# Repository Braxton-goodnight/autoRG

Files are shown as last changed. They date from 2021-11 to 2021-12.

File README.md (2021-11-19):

# autoRG
# Initial Developers: Braxton Goodnight, Rameen Forghani, Charles Latchoumane, Lohitash Karumbaiah
Includes all software code (GUI1 and GUI_scale_calibration), firmware (Arduino IDE), STL files for 3D printing, bill of commercial materials, and SOPs for the assembly of the autoRG system, downloading and initializing software, calibrating the system, and executing the assay.

# Requirements
* Matlab 2020a or newer (Earlier versions may be able to run system, but is not guaranteed)
* Windows 10 Computer
* Circuit Playground Express (CPX) (Adafruit Industries) and all other commercial electronics (see AutoRG_Assembly_SOP and Electronics_Bill_of_Materials) for CPX bootloading and assay execution

# Purpose
The autoRG system was developed to assist researchers in neurological studies of rat motor behavior. The system's hardware, software, and firmware was developed to be user-friendly, modular, reproducible, and low-cost to maximize objectivity and access to in vivo functional assessments. 

# Version 1
autoRG v1 utilizes a discrete, 7-stage training system that requires the user to manually determine when the rat has passed the criteria for that stage and select the correct stage for each rat in the menu options prior to each session. Modulation of the handle location, trigger threshold, and pellet dispenses is controlled by the update_param function. Current criterion for stage advancement using default training protocol: 
* Stage 1 - 60 successes each in two consecutive sessions
* Stage 2 - 45 successes in single session
* Stage 3 - 30 successes in single session
* Stage 4 - 30 successes in single session
* Stage 5 - 30 successes in single session
* Stage 6 - 30 successes in single session
* Stage 7 - 30 successes in single session, or until desired efficiency (# of successes / total # of reaches) is reached

# Contributions
Users can contribute to this repository by customizing the update_param function to introduce their own training schemes that train the rats more rapidly or reinforce a slightly different behavior. Further, fixes to any bugs that may arise across operating systems are encouraged. Potential training schemes to implement: 
* Continuous stage advancement - System advances rat to next stage automatically by automated measurement of some metric(s)
* Adaptive Training - System automatically progresses or modulates the trigger threshold (e.g., median of prior 10 reaches) and handle location with upper and lower boundaries
* Machine Learning - System learns which metrics are predictive of future successes or future failures and uses this information to modulate the assay parameters (handle location, trigger threshold, pellet dispenses)

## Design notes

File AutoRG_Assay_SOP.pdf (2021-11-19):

Standard Operating Procedure: Automated Reach-to-Grasp Task (AutoRG)

### 1. Purpose

1.1. This SOP describes the procedures necessary to properly utilize the hardware and software of the AutoRG system to assess forelimb motor function in rats.
1.2. This SOP utilizes the default, 7-stage training scheme provided in the standard code
1.3. This SOP assumes that the following processes are already completed:
1.3.1. The apparatus is completely assembled and primed (see: AutoRG_Assembly_SOP)
1.3.2. The software has been downloaded/integrated with a Windows computer (see: AutoRG_SoftwareInitialization_SOP)
1.3.3. The system has been calibrated and the calibration file is accessible (see: AutoRG_Calibration_SOP)

### 2. Equipment and Terminology

2.1.Cage – Refers to acrylic cage in which the rat is placed for the duration of the session

2.2. Stage – Refers collectively to the 4 stage blocks that are pre-assembled into one single stage, of which the cage is placed on top.
2.3. Handle Base – Refers to the base to which the linear motion rail is affixed
2.4. CPX – Refers to the Circuit Playground Express
2.5. CRICKIT – Refers to CRICKIT board that is attached to the CPX
2.6. Pellet Dispenser – Refers collectively to the Pellet Dispense Base and Food Silo that compose the pellet dispense apparatus
2.7. Pellet Dispense Base – Refers to base of Pellet Dispenser that has the 4 legs and includes an insertion point for the Pellet Servo
2.8. Pellet Servo Actuator – Refers to circular piece of Pellet Dispenser that connects to Pellet Servo and rotates within the Pellet Dispenser to allow pellets to be delivered
2.9. Food Silo – Refers to top of Pellet Dispenser that holds the reservoir of pellets
2.10. Pellet Dispense Tower – Refers to the tower block on which the pellet dispenser sits

2.11. Pellet Receptacle – Refers to the receptacle that receives the pellet tubing from the pellet dispenser and re-directs the pellet into the slit of the cage
2.12. Pellet Tubing – Refers to the rubber tubing that connects the pellet dispenser to the pellet receptacle (Saint-Gobain Tygon S3 E-3603 Food Tubing)
2.13. Pellet Servo – Refers to the continuous servo that actuates the pellet dispenser
2.14. Calibration Knob – Refers to knob that is used to calibrate the continuous servo
2.15. Load Cell – Refers to mini load attached to handle
2.16. Load Cell Carriage – Refers to bottom half of load cell casing that connects load cell to linear motion rail
2.17. Load Cell Handle Adapter – Refers to top half of load cell casing that connects load cell to handle
2.18. Proximal Servo Arm Adapter – Refers to servo arm adapter that connects directly to positional servo arm
2.19. Distal Servo Arm Adapter – Refers to servo arm adapter that connects the proximal servo arm to the high cube intermediate joint
2.20. High Cube Intermediate Joint – Refers to joint connecting the distal servo arm adapter to the load cell rail adapter
2.21. Handle – Refers to 1.5mm AF hex key that is affixed to the load cell apparatus
2.22. Load Cell Apparatus – Refers to load cell, load cell casing components, and rail attachment component
2.23. Rail – Refers to the 100mm-long linear motion rail on which the load cell apparatus sits
2.24. Positional Servo – Refers to the positional servo that actuates the movement of the load cell apparatus to modulate the handle distance
2.25. Positional Servo Casing – Refers to SLA-printed casing that encloses the Positional Servo and sits at the back of the Handle Base
2.26. Qwiic Scale – Refers to red analog-to-digital converter that connects the load cell to the Qwiic Adapter.

2.27. Qwiic Adapter – Refers to the component that receives a plug from the Qwiic Scale and projects wires to the CRICKIT and CPX boards.
2.28. CPX Holder – Refers to component where CPX rests; snaps into back of Pellet Dispense Tower.
2.29. Power Cord – Refers to the cord connecting the CRICKIT board to power
2.30. USB Cord – Refers to the cord connecting the CPX (micro-USB) to the computer (USB)
2.31. GUI1 – Refers to the primary MatLab graphic user interface through which the AutoRG assay is run
2.32. GUI1 Code – Refers to the code underlying GUI1
2.33. Calibration GUI – Refers to the MatLab graphic user interface that creates the calibration file
2.34. Calibration GUI Code – Refers to the code underlying the calibration GUI
2.35. Trigger Threshold: Minimum force required to trigger a successful trial and a pellet dispense

### 3. Assay Procedure

3.1. Plug in USB from CPX into the computer, ensure power cord is plugged into outlet and CRICKIT
3.2. Switch CPX on. Click reset button in center of CPX.

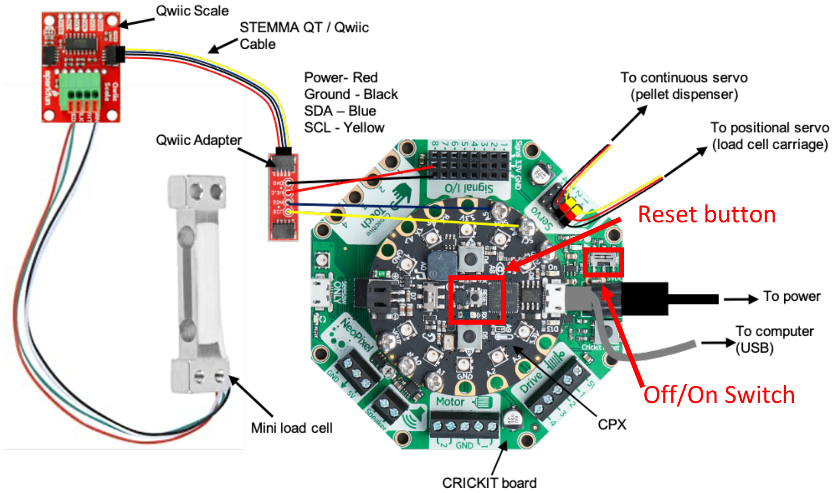
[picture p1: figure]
Reset button; Off/On Switch

3.3.Open GUI1.m on MatLab

3.4. Click “Run” to open GUI1

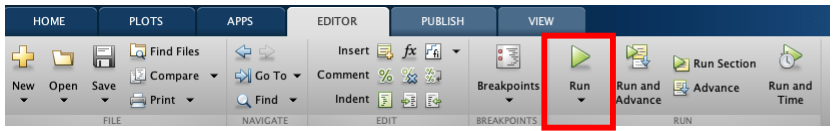
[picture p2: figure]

3.5. In the textbox beside “Port”, enter the port designation for your USB serial connection (CPX) (e.g. COM5). Click the yellow “CPX Connect” button below.
3.5.1. To check the port designation for your CPX, go to Device Manager > Click on “Ports” > See port designation for “USB Serial Connection”
3.5.2. Entering the COM designation directly in the GUI1 code saves a default COM designation so that you do not have to type in the designation each time (see: AutoRG_SoftwareInitialization_SOP). Note that the COM designation will change if a different CPX is used.
3.5.3. Check that a green “COM[] CONNECTED” box appears (where [] is the number of your COM designation)

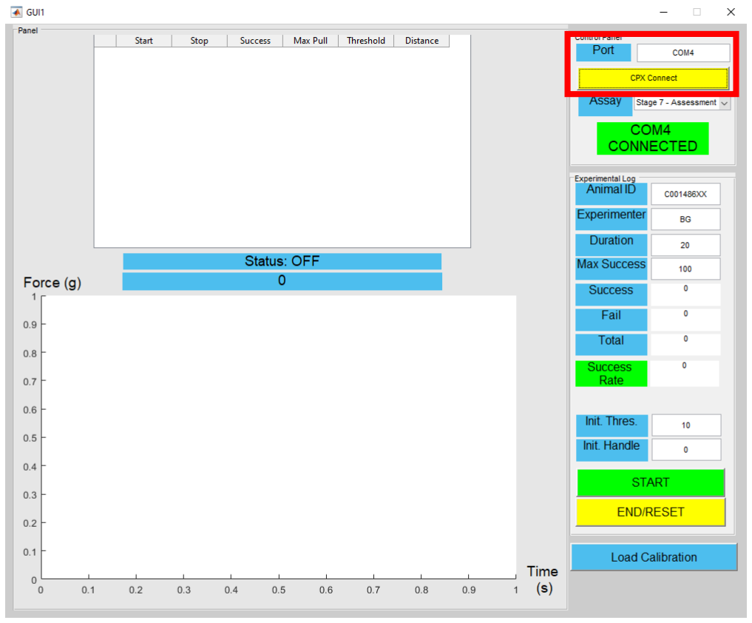
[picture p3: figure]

3.6. Select the Appropriate stage for the current rat in the dropdown box beside “Assay”

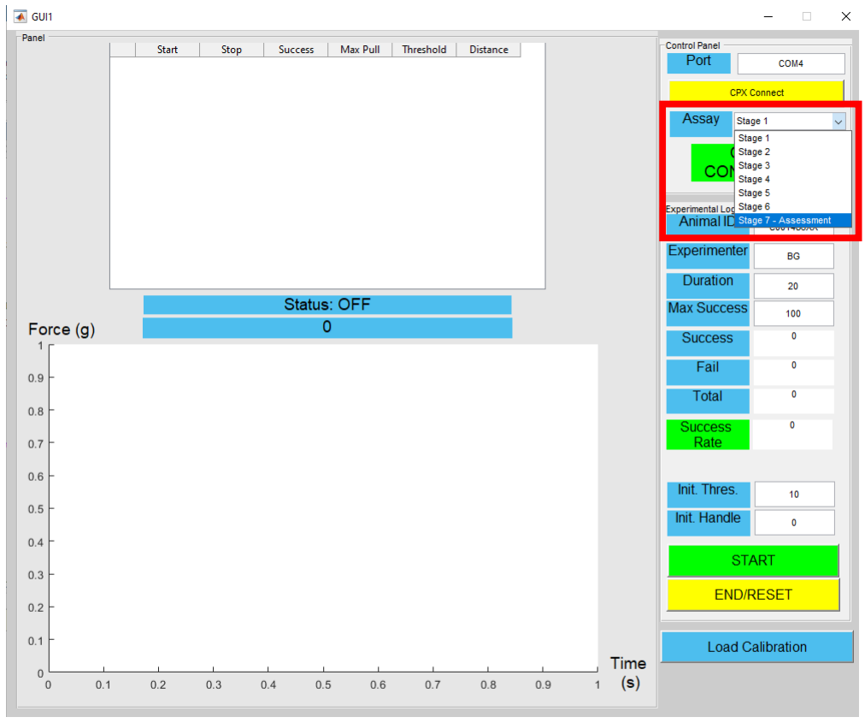
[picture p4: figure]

3.7. Enter any identifying number/code for the current rat in the textbox beside “Animal ID”

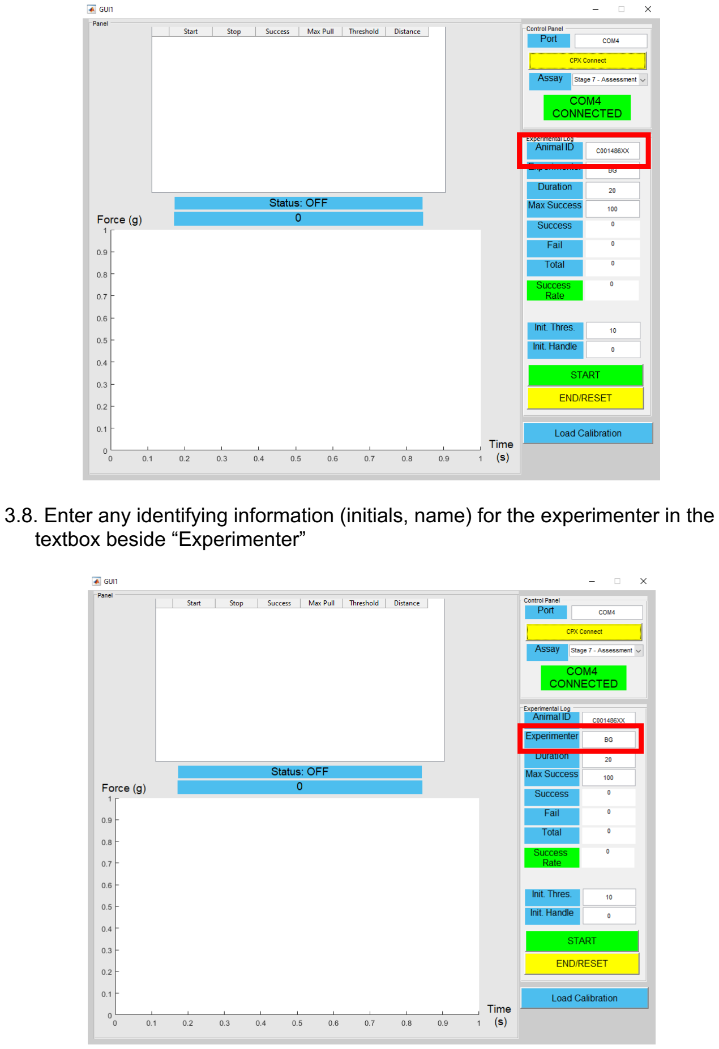
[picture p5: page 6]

3.8. Enter any identifying information (initials, name) for the experimenter in the textbox beside “Experimenter”

3.9. To change the default session duration: Enter desired session duration in minutes in the textbox beside “Duration”
3.9.1. Default: 20 minutes
3.9.2. If user desires to change session duration permanently, it is recommended to make this change directly in the GUI1 code. See AutoRG_SoftwareCustomization for more information

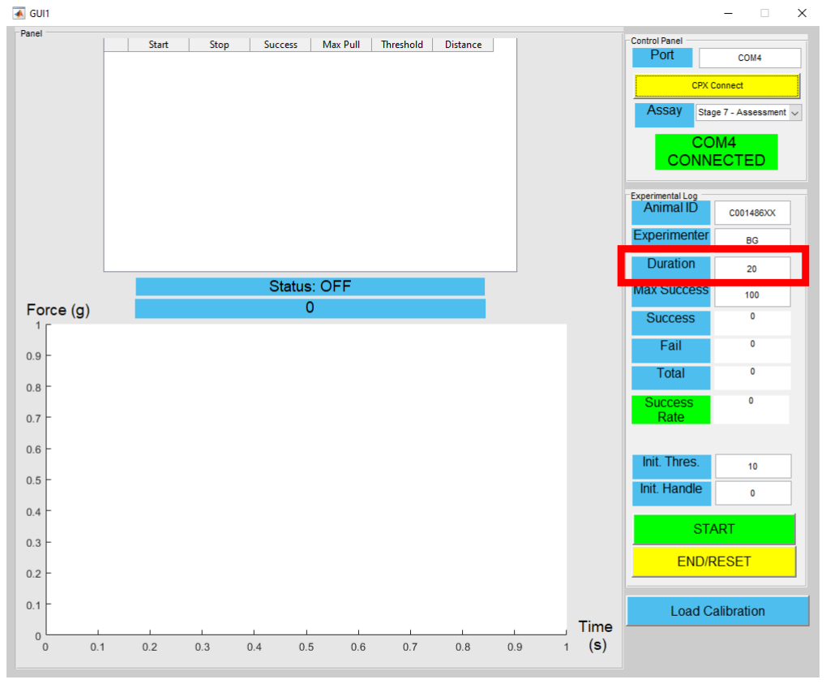
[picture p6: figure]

3.10. To change the default maximum number of successful trials for a given session: Enter desired maximum number of successful trials in the textbox beside “Max Success”
3.10.1. Default: 100 successes
3.10.2. If user desires to change maximum successes permanently, it is recommended to make this change directly in the GUI1 code. See AutoRG_SoftwareCustomization for more information

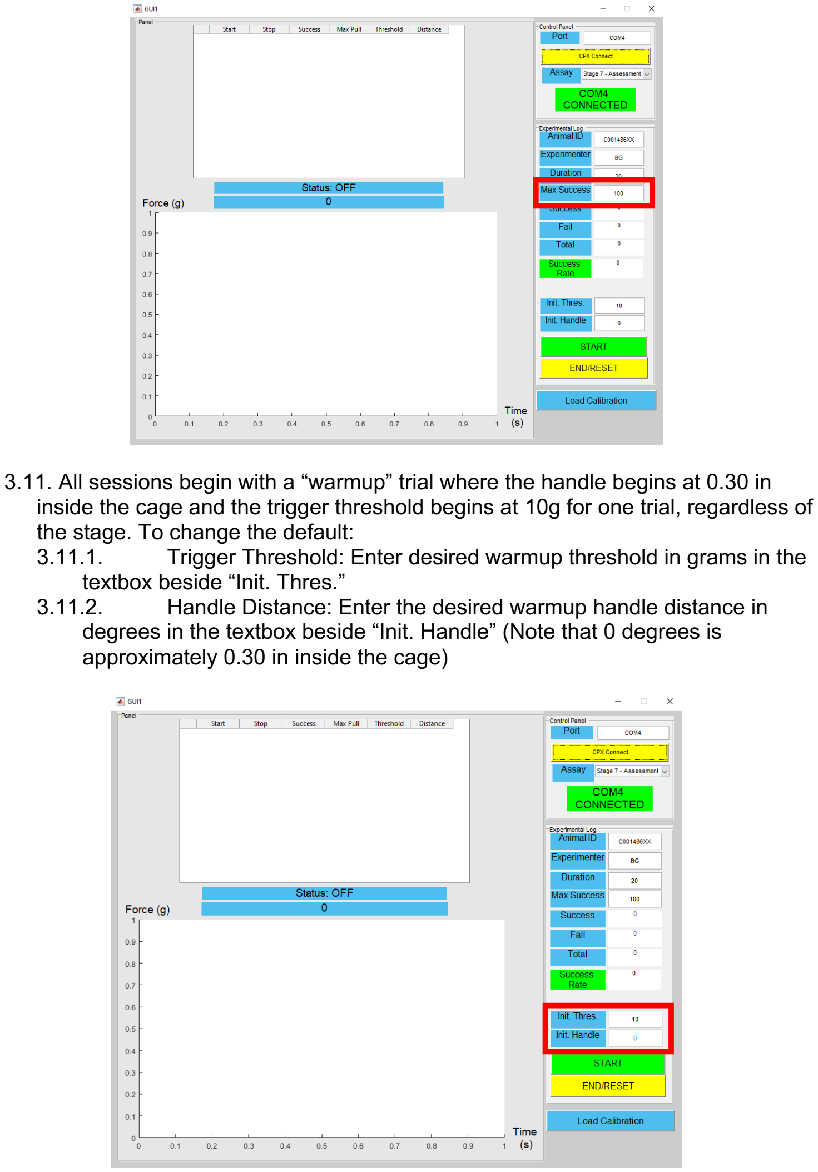
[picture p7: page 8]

3.11. All sessions begin with a “warmup” trial where the handle begins at 0.30 in inside the cage and the trigger threshold begins at 10g for one trial, regardless of the stage. To change the default:
3.11.1. Trigger Threshold: Enter desired warmup threshold in grams in the textbox beside “Init. Thres.”
3.11.2. Handle Distance: Enter the desired warmup handle distance in degrees in the textbox beside “Init. Handle” (Note that 0 degrees is approximately 0.30 in inside the cage)

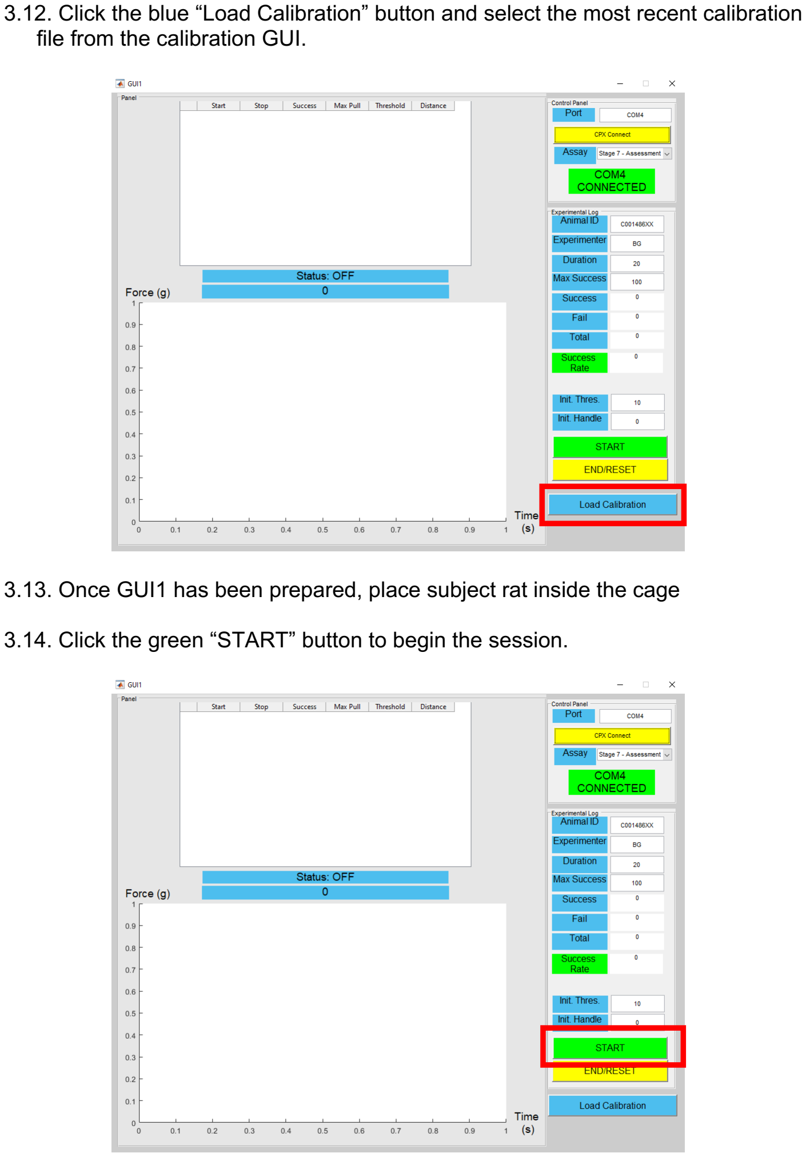
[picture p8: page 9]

3.12. Click the blue “Load Calibration” button and select the most recent calibration file from the calibration GUI.
3.13. Once GUI1 has been prepared, place subject rat inside the cage
3.14. Click the green “START” button to begin the session.

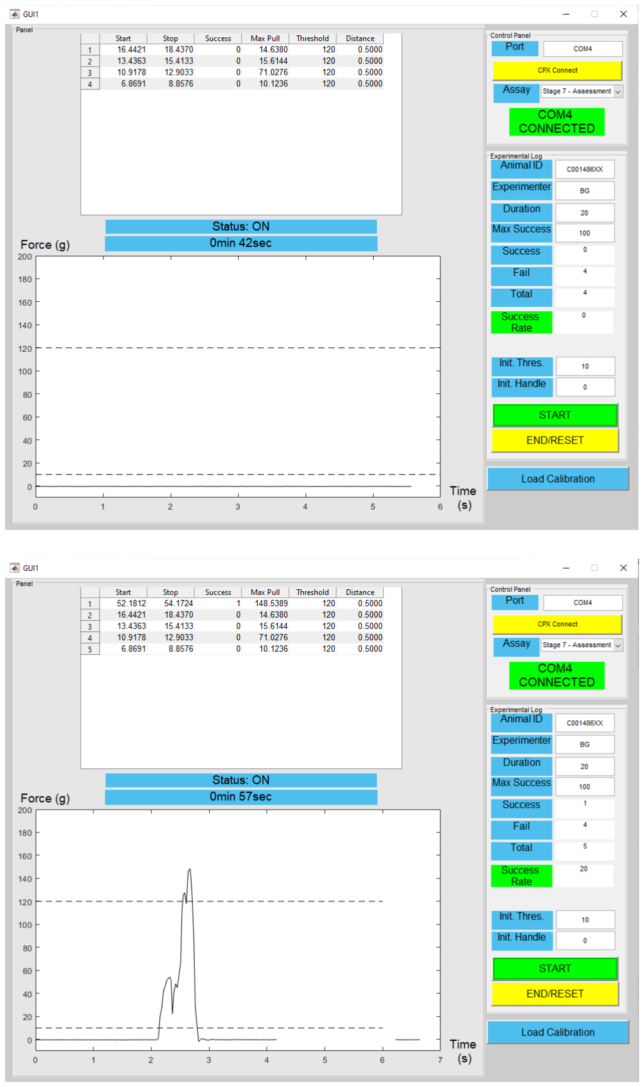
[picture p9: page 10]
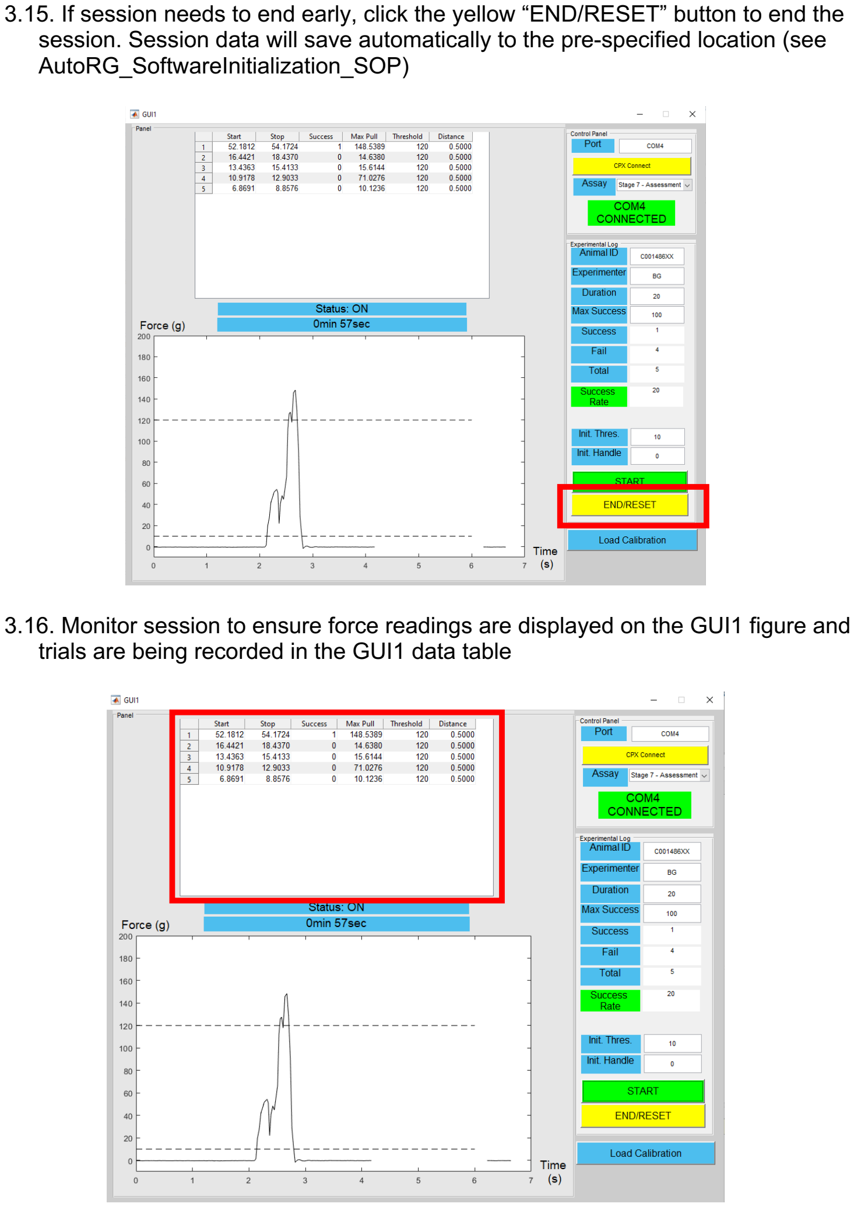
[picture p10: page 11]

3.15. If session needs to end early, click the yellow “END/RESET” button to end the session. Session data will save automatically to the pre-specified location (see AutoRG_SoftwareInitialization_SOP)
3.16. Monitor session to ensure force readings are displayed on the GUI1 figure and trials are being recorded in the GUI1 data table

3.17. At the end of the session, session data will automatically save to the pre-specified location. Remove the rat from the cage. Click yellow “END/RESET” button to clear GUI1
3.18. Port designation should not be affected by reset. Re-click yellow “CPX Connect” button
3.19. Repeat 3.4 – 3.9 as needed. Port designation, Animal ID, and Experimenter ID should not reset. Enter next animal ID’s, and select the stage for this next rat. Place rat in cage, and click green “START” button to begin next session.
3.20. Repeat 3.13 – 3.17 for each session
3.21. After all sessions are complete: Clean cage with veterinary approved cleaner. Remove and rinse pellet receptacle to avoid pellet dust buildup. Place somewhere to dry. Switch CPX off. Unplug USB from computer.

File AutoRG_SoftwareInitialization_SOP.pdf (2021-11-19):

Standard Operating Procedure: Automated Reach-to-Grasp Task (AutoRG) Software/Firmware Download and Initialization Portions of this SOP have been adapted from learn.adafruit.com

### 1. Purpose

1.1. This SOP describes the procedures necessary to properly download and initialize the software (Matlab) and firmware for the AutoRG system.

### 2. Equipment and Terminology

2.1. CPX – Refers to the Circuit Playground Express
2.2. CRICKIT – Refers to CRICKIT board that is attached to the CPX
2.3. Power Cord – Refers to the cord connecting the CRICKIT board to power
2.4. USB Cord – Refers to the cord connecting the CPX (micro-USB) to the computer (USB)
2.5. GUI1 – Refers to the primary MatLab graphic user interface through which the AutoRG assay is run

2.6.GUI1 Code – Refers to the code underlying GUI1

2.7. Calibration GUI – Refers to the MatLab graphic user interface that creates the calibration file
2.8. Calibration GUI Code – Refers to the code underlying the calibration GUI

### 3. Download and Initialization Procedure

3.1. Download software and firmware files from Github:
3.1.1. FIRMWARE_11.2021_CPX.UF2
3.1.2. FIRMWARE_11.2021_crickit.UF2
3.1.3. GUI1.m and GUI1.fig
3.1.4. GUI_scale_calibration.m and GUI_scale_calibration.fig
3.2. Plug Power Cord into CPX/Crickit system (power port is located on Crickit component of system)
3.3. Turn Crickit on with switch near power
3.3.1. Green light near switch should appear when switch is on

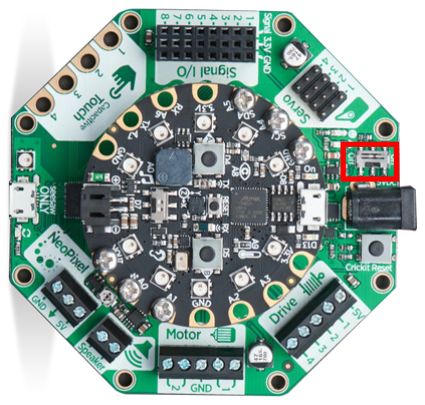
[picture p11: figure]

3.4. Plug data-sync USB cable into “Seesaw ONLY” port on Crickit, and plug other side of USB cord into computer.

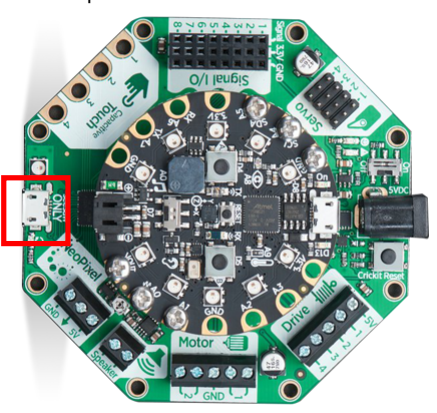
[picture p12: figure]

3.5. Double-click the Crickit Reset button

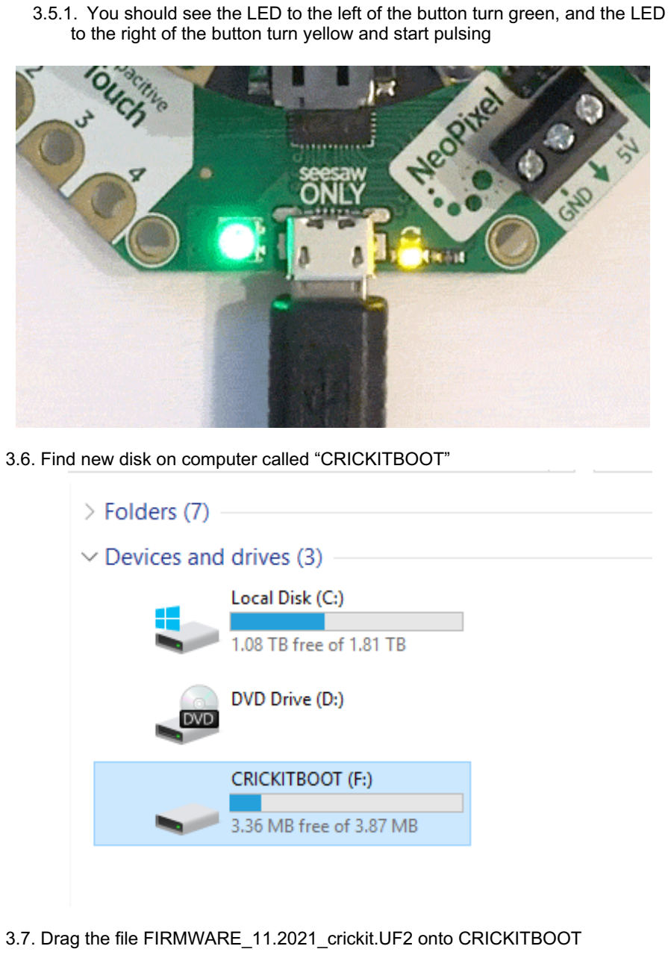
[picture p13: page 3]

3.5.1. You should see the LED to the left of the button turn green, and the LED to the right of the button turn yellow and start pulsing
3.6. Find new disk on computer called “CRICKITBOOT”
3.7. Drag the file FIRMWARE_11.2021_crickit.UF2 onto CRICKITBOOT

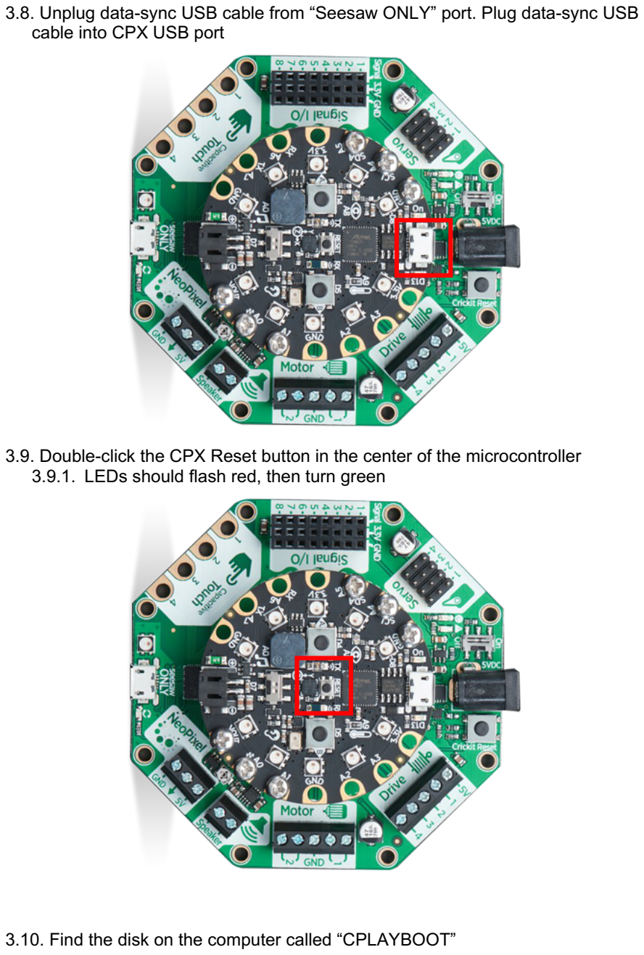
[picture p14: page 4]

3.8. Unplug data-sync USB cable from “Seesaw ONLY” port. Plug data-sync USB cable into CPX USB port
3.9. Double-click the CPX Reset button in the center of the microcontroller
3.9.1. LEDs should flash red, then turn green
3.10. Find the disk on the computer called “CPLAYBOOT”

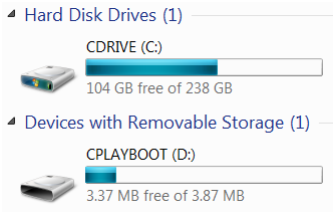
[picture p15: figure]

3.11. Drag the file FIRMWARE_11.2021_CPX.UF2 onto CPLAYBOOT
3.12. Open GUI1.m
3.13. Use Ctrl + F “ %EDIT ” to find all lines marked with an EDIT comment. These lines need to modified to integrate with user’s computer
3.13.1. handles.Com : Recommended for user to replace ‘COM4’ with the COM port on their PC. To find COM port of CPX, ensure USB is plugged into CPX and computer, then navigate to “Device Manager” on PC. Navigate to “Ports”, then find the COM input for the CPX serial connection. Note:
COM number can be inputted directly into GUI but inputting here directly into code allows the convenience of not having to continually re-input the COM number with each training session.
3.13.2. handles.Animal : Recommended for user to replace this default template with a template that is convenient to the animal identification coding utilized by user’s facility/institution. Note: Animal ID can be inputted directly into GUI but inputting here directly allows the convenience of having to change only a few digits while training many animals.
3.13.3. handles.ExpName : Recommended for user to replace initials with experimenter identification that is convenient for user. Can be inputted directly into GUI as well, but inputs directly into GUI will be erased when GUI is closed.
3.13.4. handles.Assay : If using the default 7-stage training protocol, no action must be taken here. If implementing custom training protocol: Add or substitute name of custom protocol in the same format (separated from other lines by semicolon (;), name inputted as a string (e.g. ‘PROTOCOL NAME’ ).

3.13.5. handles.Duration : If desired to change default duration of training session, alter the number inside the quotations to the desired number of minutes. Default session duration is 20 minutes, after which the session will end, and the data will be saved to pre-specified PC location. Duration can be modified directly on GUI, though it will be erased each time the GUI is closed and reopened.
3.13.6. handles.MaxSuccess : If desired to change default maximum number of successes for a training session, alter the number to the desired number of successes. Default max number of successes is 100, after which the session will end, and the data will be saved to pre-specified PC location. Maximum successes can be modified directly on GUI, though it will be erased each time the GUI is closed and reopened.
3.13.7. handles.Threshold : If desired to change the minimum threshold to initiate a trial, alter the number to the desired minimum threshold (in grams). Default initiation threshold is 10g.
3.13.8. handles.savename : Default save name is set to “ANIMALID_EXPERIMENTERID_ASSAYNAME_DATE”. Remove or add variables to customize this save name.
3.13.9. lowthr : Change this number to match the value inputted for handles.Threshold
3.13.10. maxtime : If desired to change the trial time, alter the number to the desired trial duration in seconds. Default trial time is 2 seconds.
3.13.11. Save Locations: Wherever “ %EDIT save location” is found, input the desired save location for the output .mat files. To find this location name:
3.13.11.1. Navigate to the folder using the file window on user’s PC.
3.13.11.2. Right-click on the address bar at the top and click “Copy address as text”.
3.13.11.3. Delete the save location address beginning with C:\
3.13.11.4. Paste the copied address within the quotations
3.13.11.5. Repeat this process for every line denoted by “%EDIT save location” : Delete old save location within the quotations and paste the new copied address in its place. As of November 2021, there should be 12 lines that must be updated with the user’s save location.

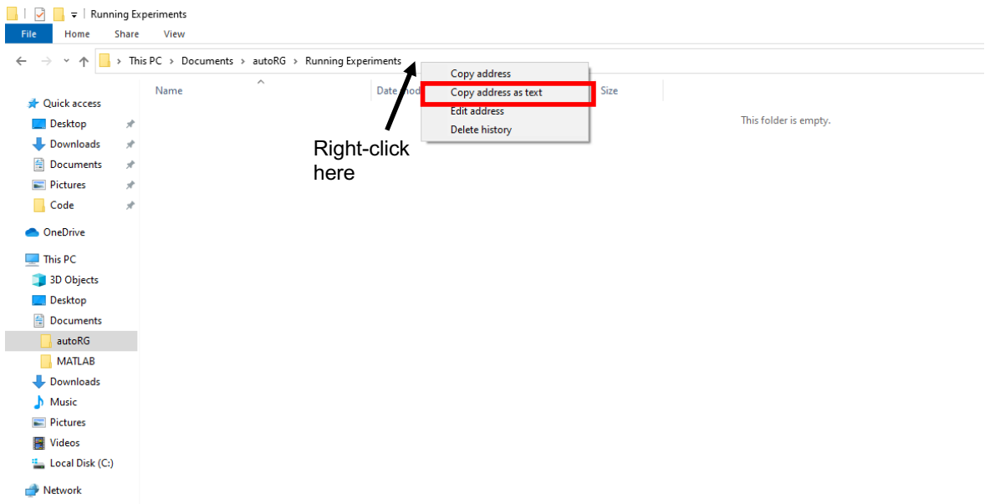
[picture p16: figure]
Right-click here

3.13.12. Only use this section is custom protocol is added. Otherwise, disregard this section. For custom protocol is lines denoted by “ %EDIT if custom protocol added “:
3.13.12.1. Around Line 437 (as of 11/2021): “ switch handles.AssayIdx “ section: Add “case“ followed by number corresponding to the location of the name of the custom protocol for handles.Assay (e.g., if custom protocol name ‘CUSTOM’ is added after ‘Stage 7 – Assessment’, such as […; ‘Stage 7 – Assessment’ ; ‘CUSTOM’ ], then “case 8” should be added to this section). Below, input the distance (in inches) of the handle relative to the inner wall or the variable corresponding to the distance if adaptive distance used. Distance inputted here is displayed in output trialdata matrix.

case 8
dist = ____ ;
3.13.12.2. Around Line 588 (as of 11/2021): “ switch selectedString “ section: Add “case“ followed by the string used for handles.Assay (e.g., if custom protocol name ‘CUSTOM’ is added then “case ‘CUSTOM’ ” should be added to this section). Below, input “ stage = “ followed by some identification number (e.g., 8) or alternative ID. Stage/Protocol ID inputted here is displayed in output summary matrix.

case ‘CUSTOM’
stage = 8 ;

3.13.12.3. Around Line 737 (as of 11/2021): “ switch selectedString “ section: Add “case“ followed by the string used for handles.Assay (e.g., if custom protocol name ‘CUSTOM’ is added then “case ‘CUSTOM’ ” should be added to this section). Below, input “ handles.AssayIdx = “ followed by the next available number.
3.13.12.3.1. If custom protocol name ‘CUSTOM’ is added after ‘Stage 7 – Assessment’, such as […; ‘Stage 7 – Assessment’ ; ‘CUSTOM’ ], then use “handles.AssayIdx = 8”

case ‘CUSTOM’
handles.AssayIdx = 8 ;
3.13.12.3.2. If default stages removed for handles.Assay in step 3.13.4, then begin the numbering at 2 and continue from that number. Beginning numbering at 2 bypasses several lines that check if the system is past Stage 1. However, if user is not using default 7-stage protocol, these check points are irrelevant.

case ‘CUSTOM 1’
handles.AssayIdx = 2 ;

case ‘CUSTOM 2’
handles.AssayIdx = 3 ;

... and so on

3.13.12.4. Around Line 830 (as of 11/2021): Copy and paste section from 3.13.12.2 (around Line 737) to replace this section, from “ switch “ to corresponding “end” .
3.13.13. Reset Function, below comment “%Re-initialize all text and variables”: Copy the initialization sections between the “%AUTORG INITIALIZATION ONLY” markings, which includes all lines between “%Control Variables” near Line 36 to “ guidata(hObject, handles); “ near Line 105. Highlight the lines between “ %BEGIN PASTE HERE ” and “ %END PASTE HERE ” and paste the copied lines in its place.
3.13.14. edit_Threshold : If default trial initiation threshold threshold changed (see steps 3.13.7 and 3.13.9), then alter the text here to match the customized threshold

End of GUI1 Initialization
3.14. Open GUI_scale_calibration.m

3.15. Use Ctrl + F “ %EDIT ” to find all lines marked with an EDIT comment. These lines need to modified to integrate with user’s computer
3.15.1. handles.COM : Update COM as in step 3.13.1
3.16. If custom protocol implemented: “inside”, “onwall”, “outside”, and “assessment” variables. These values are only relevant when using one of default 7 stages.

The following steps are only relevant if custom protocol added

3.17. If adding custom protocol: Open update_param.m function
3.18. Add “case” followed by the AssayID corresponding to the handles.AssayIdx variable created for the custom protocol in GUI1 (see step 3.13.12.3 ).
3.19. Insert custom algorithm that updates the handle position, trigger threshold, trial time, etc. utilizing inputs from GUI1

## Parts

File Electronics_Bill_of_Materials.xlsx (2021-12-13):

Part | Manufacturer | Catalog | Quantity needed | Unit price
Circuit Playground express | Adafruit | 3333 | 1 | 24.95
Adafruit CRICKIT for circuit playground express | Adafruit | 3093 | 1 | 29.95
Continuous Rotation Servo - Feetech FS5103R | Adafruit/Feetech | 154 | 1 | 11.95
Micro servo - high powered high torque metal gear | Adafruit | 2307 | 1 | 11.95
Mini Load Cell - 500g, Straight Bar (TAL221) | Sparkfun | SEN-14728 | 1 | 9.95
SparkFun Qwiic Scale - NAU7802 | Sparkfun | SEN-15242 | 1 | 14.95
Linear Motion Rail, 100mm×9mm MGN9H Bearing Steel Miniature Linear Rail Guide Rail + Carriage Slide Block Used for Automatic Equipment,etc | Yanmis | MGN9H | 1 | 15.59
Sparkfun STEMMA QT / Qwiic Adapter | Adafruit/Sparkfun | 4527 | 1 | 1.95
STEMMA QT/Qwiic cable (200mm long) | Adafruit | 4401 | 1 | 0.95
5V 4A Switching Power Supply | Adafruit | 1466 | 1 | $14.95
 |  |  |  | 137.14

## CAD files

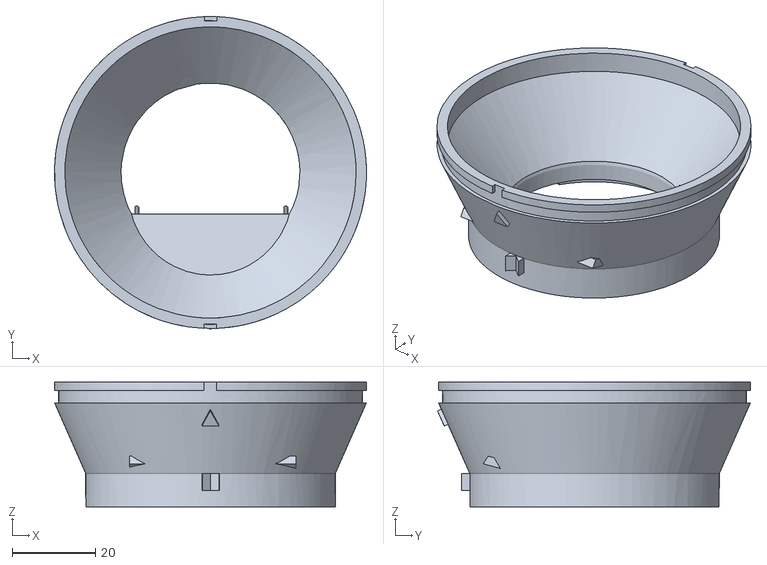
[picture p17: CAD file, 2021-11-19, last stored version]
Food Silo.stl
75.0 x 75.2 x 30.0

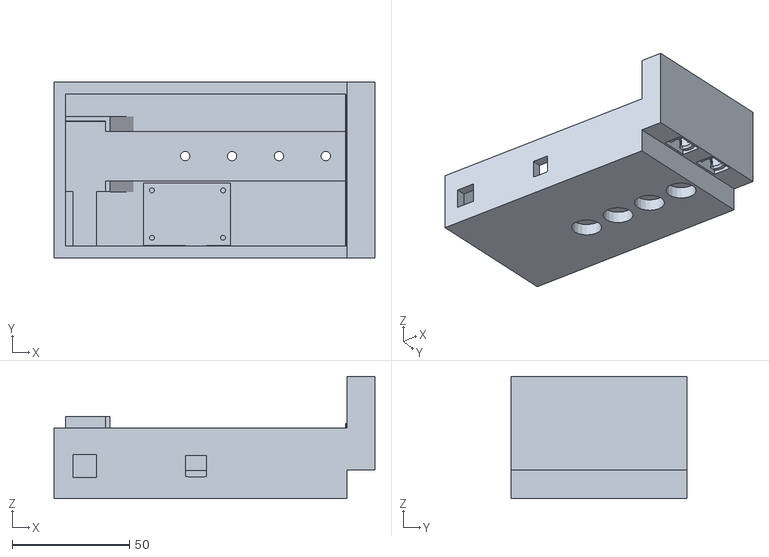
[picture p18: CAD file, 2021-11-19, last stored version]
Handle Base.stl
137.0 x 75.0 x 52.1

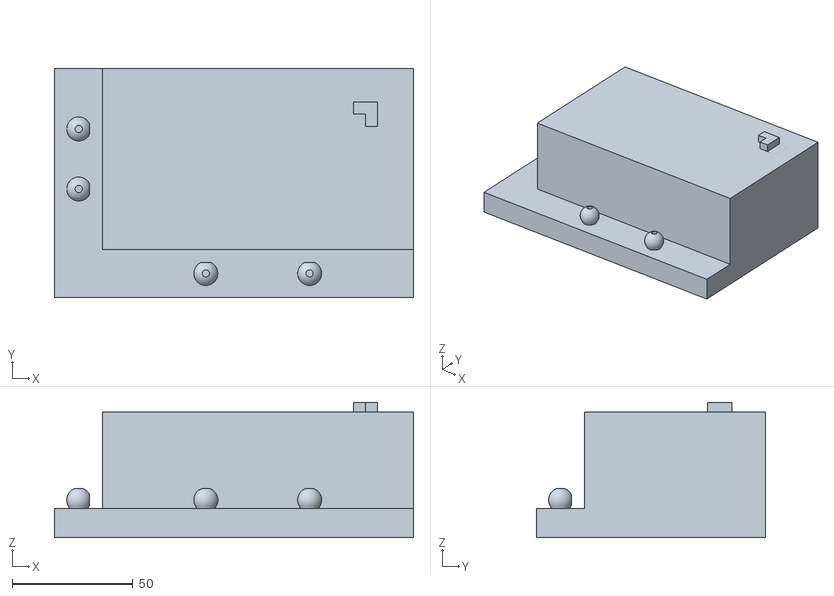
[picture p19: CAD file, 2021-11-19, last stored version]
Q3_Stage.stl
148.7 x 95.0 x 56.0

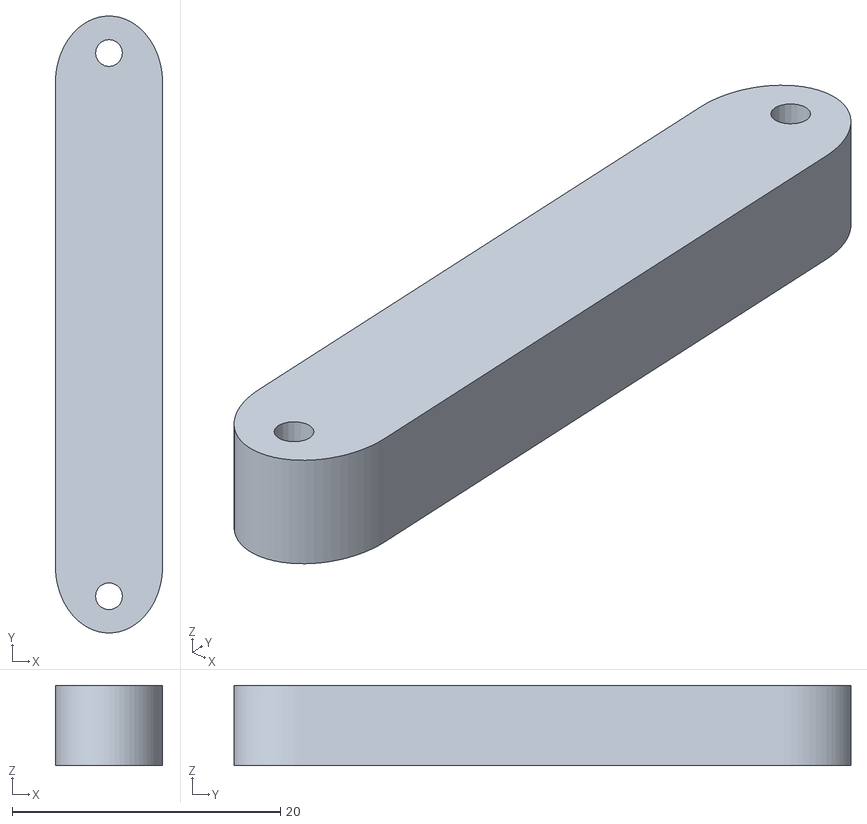
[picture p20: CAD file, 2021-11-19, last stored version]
Distal Servo Arm Adapter.stl
8.00 x 46.0 x 6.00

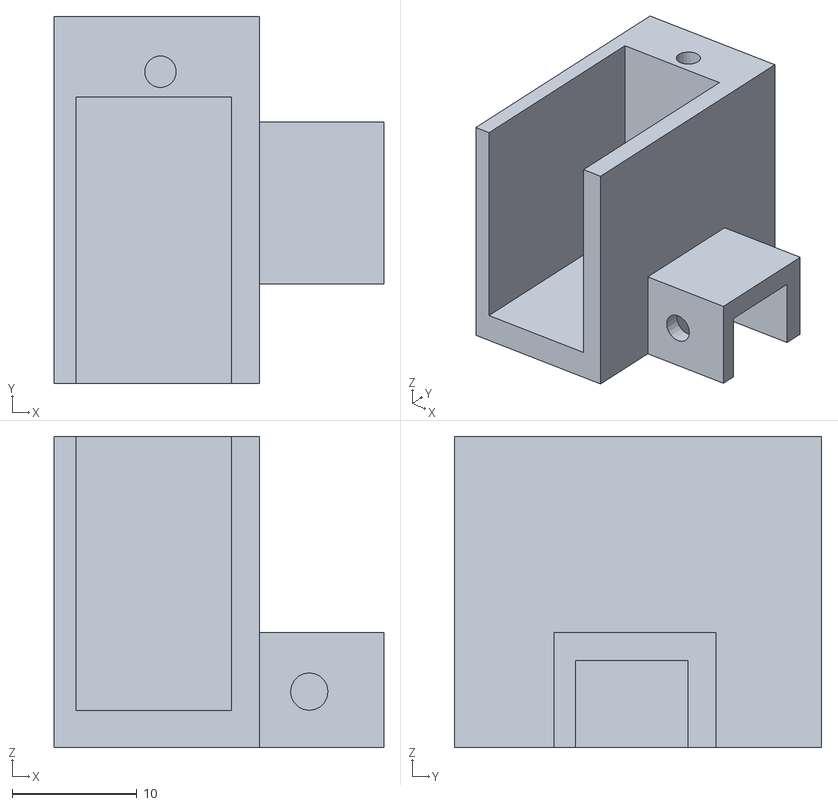
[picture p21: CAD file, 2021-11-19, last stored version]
Positional Servo Casing.stl
26.5 x 29.5 x 25.0

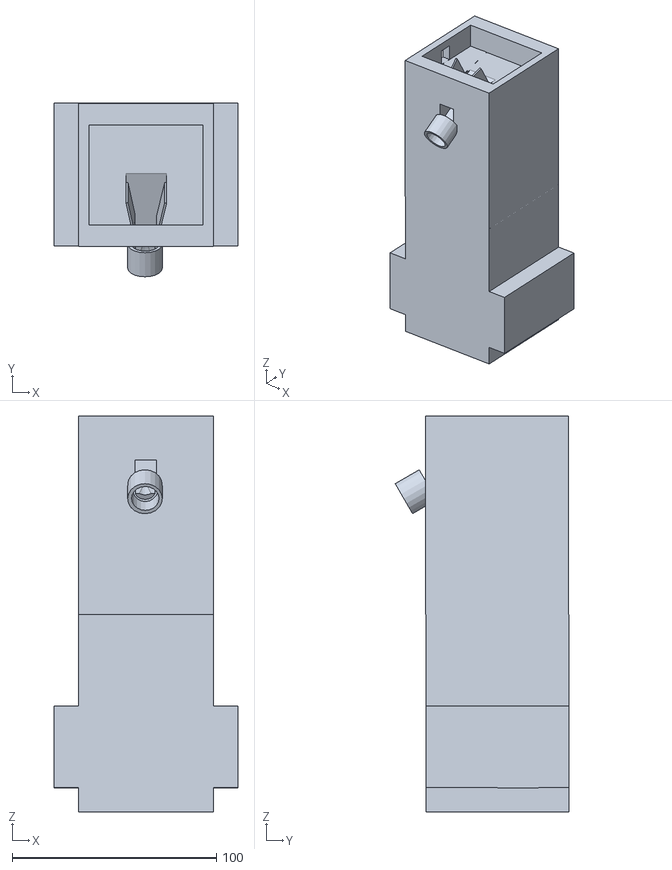
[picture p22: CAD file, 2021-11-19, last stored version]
Pellet Dispense Tower.stl
90.0 x 85.1 x 194.1

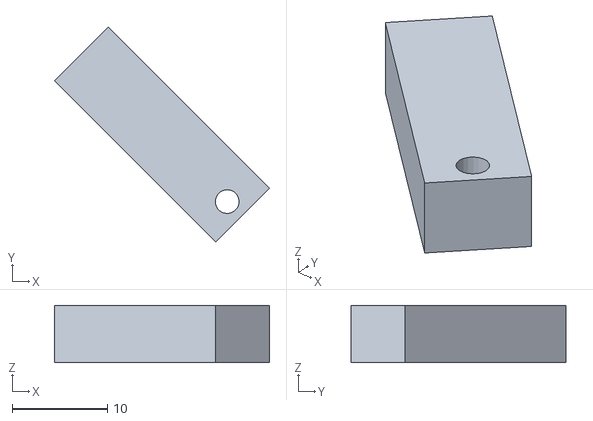
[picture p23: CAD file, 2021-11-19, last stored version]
Proximal Servo Arm Adapter.stl
22.6 x 22.6 x 6.00

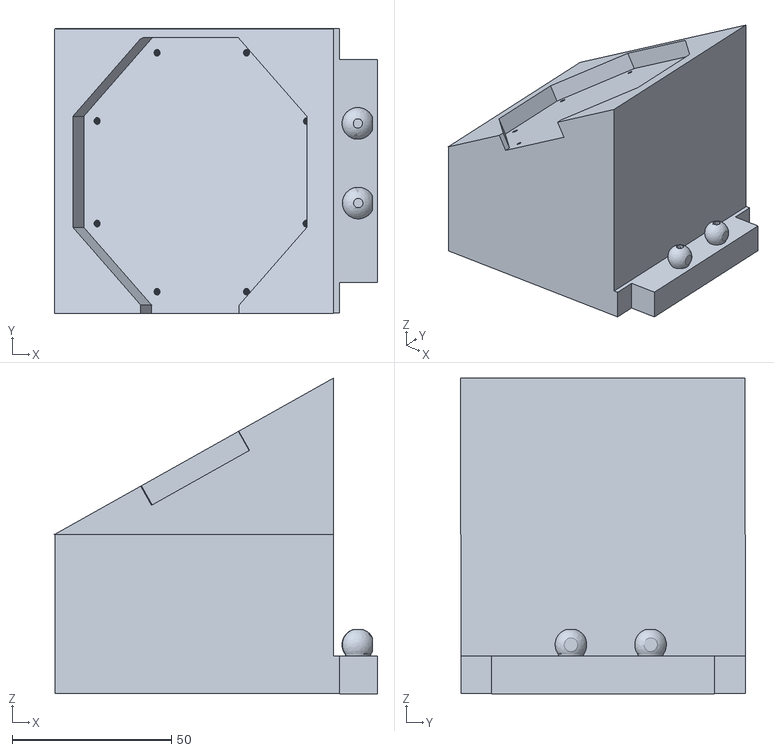
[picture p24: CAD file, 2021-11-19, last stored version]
CPX Holder.stl
101.4 x 89.4 x 99.2

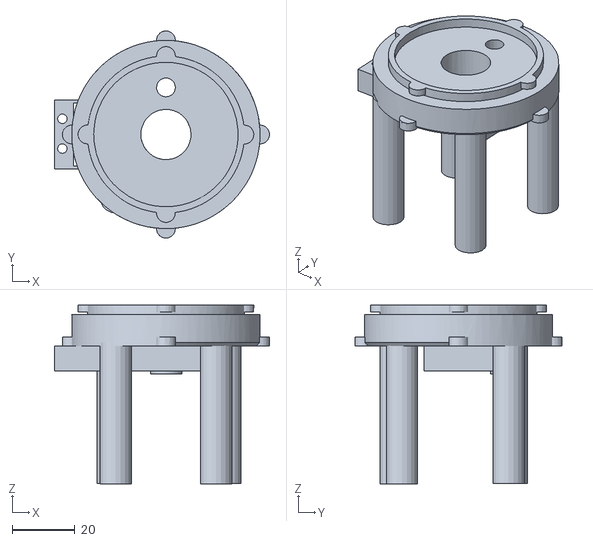
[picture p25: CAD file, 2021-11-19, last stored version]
Pellet Dispense Base.stl
68.5 x 66.0 x 57.0

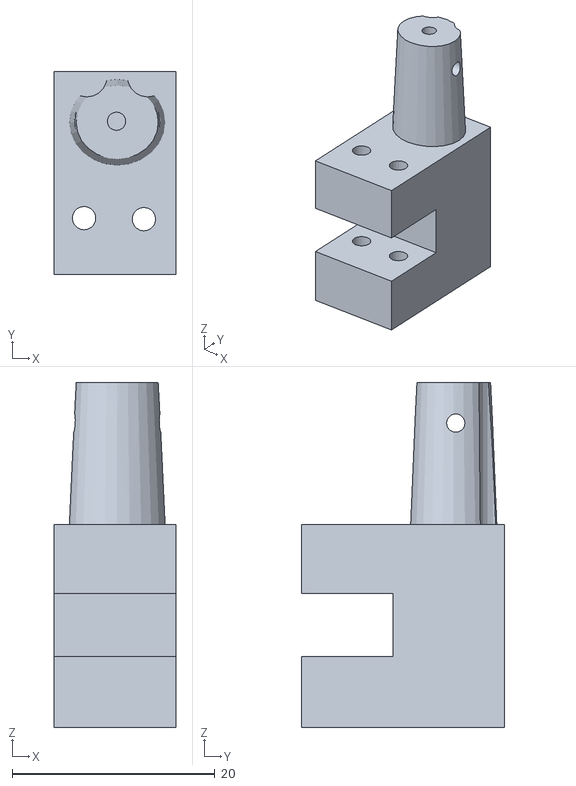
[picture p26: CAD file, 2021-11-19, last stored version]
Load Cell Handle Adapter.stl
12.0 x 20.0 x 34.0

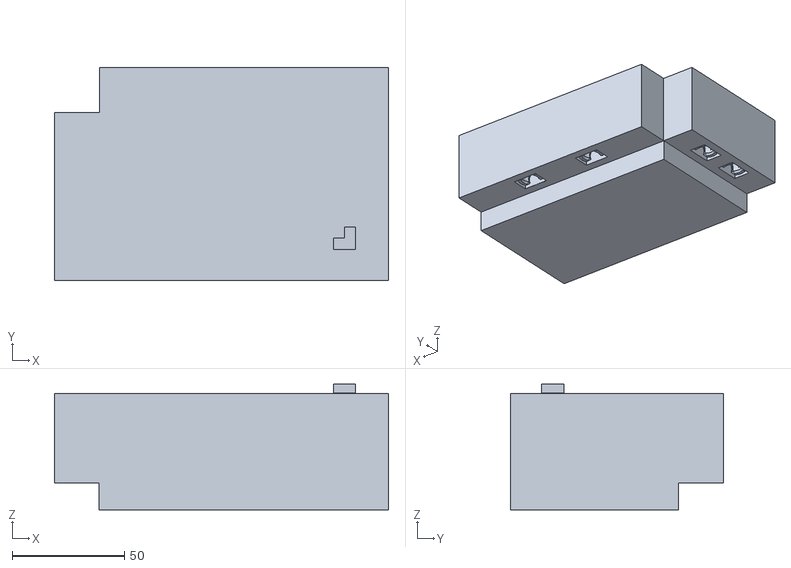
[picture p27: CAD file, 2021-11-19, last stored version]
Q2_Stage.stl
148.9 x 95.0 x 56.1

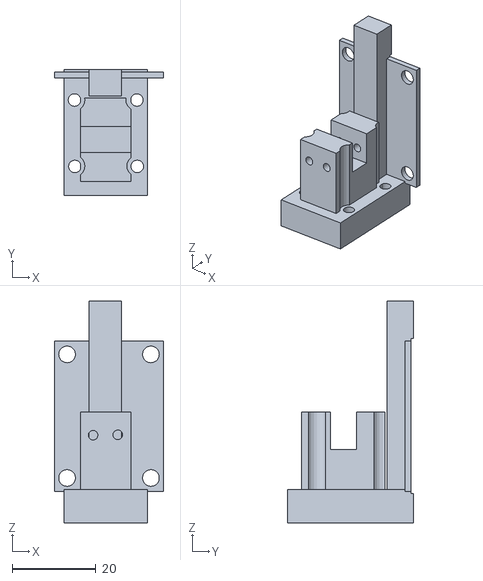
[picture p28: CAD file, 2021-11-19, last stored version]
Load Cell Carriage.stl
26.0 x 30.0 x 53.0

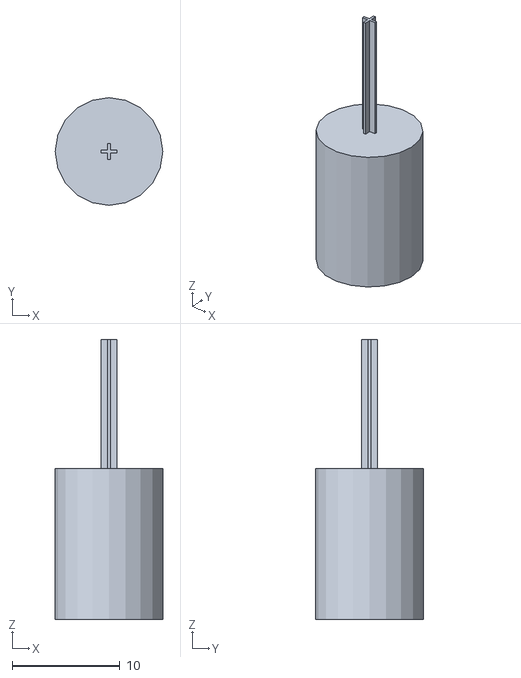
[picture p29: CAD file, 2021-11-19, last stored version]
Calibration Knob for ContinuousServo.stl
10.0 x 10.0 x 26.0

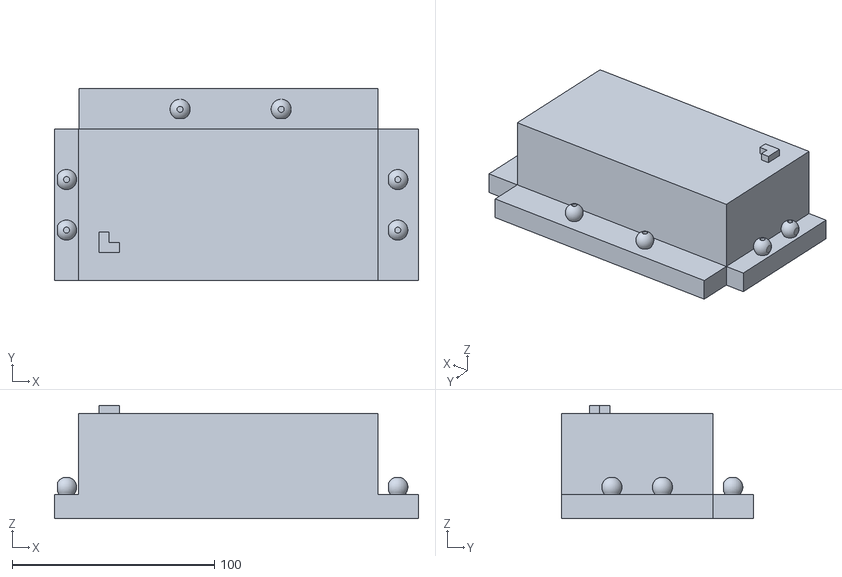
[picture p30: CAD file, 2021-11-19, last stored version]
Q1_Stage.stl
180.0 x 95.0 x 56.1

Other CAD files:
HighCube Intermediate Joint.stl
Q4_Stage.stl
Pellet Receptacle.stl
Thin Box Corner Block.stl
Pellet Servo Actuator.stl

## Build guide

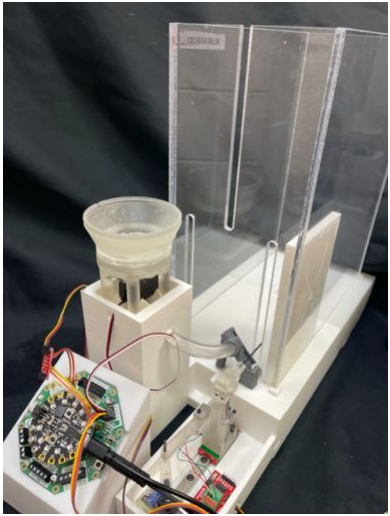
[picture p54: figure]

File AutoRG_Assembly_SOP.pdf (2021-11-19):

Standard Operating Procedure: Automated Reach-to-Grasp Task (AutoRG) System Assembly

### 1. Purpose

1.1. This SOP describes the procedures necessary to properly assemble the hardware of the AutoRG system.
1.2. This SOP assumes that the following processes are already completed:
1.2.1. The software has been downloaded/initialized with a Windows computer (see: AutoRG_SoftwareInitialization_SOP)

### 2. Equipment and Terminology

2.1. Cage – Refers to acrylic cage in which the rat is placed for the duration of the session
2.2. Stage – Refers collectively to the 4 stage blocks that are pre-assembled into one single stage, of which the cage is placed on top (Extrusion-PLA 3D print)
2.3. Handle Base – Refers to the base to which the linear motion rail is affixed (Extrusion-PLA 3D print)
2.4. CPX – Refers to the Circuit Playground Express
2.5. CRICKIT – Refers to CRICKIT board that is attached to the CPX
2.6. Pellet Dispenser – Refers collectively to the Pellet Dispense Base and Food Silo that compose the pellet dispense apparatus (SLA-resin 3D print)
2.7. Pellet Dispense Base – Refers to base of Pellet Dispenser that has the 4 legs and includes an insertion point for the Pellet Servo (SLA-resin 3D print)
2.8. Pellet Servo Actuator – Refers to circular piece of Pellet Dispenser that connects to Pellet Servo and rotates within the Pellet Dispenser to allow pellets to be delivered (SLA-resin 3D print)
2.9. Food Silo – Refers to top of Pellet Dispenser that holds the reservoir of pellets (SLA-resin 3D print)
2.10. Pellet Dispense Tower – Refers to the tower block on which the pellet dispenser sits (Extrusion-PLA 3D print)
2.11. Pellet Receptacle – Refers to the receptacle that receives the pellet tubing from the pellet dispenser and re-directs the pellet into the slit of the cage (Extrusion-PLA 3D print)

2.12. Pellet Tubing – Refers to the rubber tubing that connects the pellet dispenser to the pellet receptacle (Saint-Gobain Tygon S3 E-3603 Food Tubing)
2.13. Pellet Servo – Refers to the continuous servo that actuates the pellet dispenser
2.14. Calibration Knob – Refers to knob that is used to calibrate the continuous servo (SLA-resin 3D print)
2.15. Load Cell – Refers to mini load attached to handle
2.16. Load Cell Carriage – Refers to bottom half of load cell casing that connects load cell to linear motion rail (SLA-resin 3D print)
2.17. Load Cell Handle Adapter – Refers to top half of load cell casing that connects load cell to handle (SLA-resin 3D print)
2.18. Proximal Servo Arm Adapter – Refers to servo arm adapter that connects directly to positional servo arm (SLA-resin 3D print)
2.19. Distal Servo Arm Adapter – Refers to servo arm adapter that connects the proximal servo arm to the high cube intermediate joint (SLA-resin 3D print)
2.20. High Cube Intermediate Joint – Refers to joint connecting the distal servo arm adapter to the load cell rail adapter (SLA-resin 3D print)
2.21. Handle – Refers to 1.5mm AF hex key that is affixed to the load cell apparatus
2.22. Load Cell Apparatus – Refers to load cell, load cell casing components, and rail attachment component
2.23. Rail – Refers to the 100mm-long linear motion rail on which the load cell apparatus sits
2.24. Positional Servo – Refers to the positional servo that actuates the movement of the load cell apparatus to modulate the handle distance
2.25. Positional Servo Casing – Refers to SLA-printed casing that encloses the Positional Servo and sits at the back of the Handle Base (SLA-resin 3D print)
2.26. Qwiic Scale – Refers to red analog-to-digital converter that connects the load cell to the Qwiic Adapter.
2.27. Qwiic Adapter – Refers to the component that receives a plug from the Qwiic Scale and projects wires to the CRICKIT and CPX boards.

2.28. CPX Holder – Refers to component where CPX rests; snaps into back of Pellet Dispense Tower.
2.29. Power Cord – Refers to the cord connecting the CRICKIT board to power
2.30. USB Cord – Refers to the cord connecting the CPX (micro-USB) to the computer (USB)
2.31. Other assembly materials:
2.31.1. All-Purpose Krazy Glue
2.31.2. 1.5, 2, 2.5mm AF Hex Keys
2.31.3. Parafilm M
2.31.4. Fasteners:
2.31.4.1. M3-0.5 x 6mm Sock Cap Screw (High Cube Intermediate Joint to Load Cell Carriage)
2.31.4.2. M3-0.5 x 12mm Socket Cap Screws (Rail to Handle Base)
2.31.4.3. M3-0.5 x 16mm Socket Cap Screws (Load Cell Carriage to Rail)
2.31.4.4. M2.5-0.45 x 25mm (total length) / 20mm (threaded length) screw (Distal Servo Arm Adapter to High Cube Intermediate Joint) (Proximal Servo Arm Adapter to Distal Servo Arm Adapter) (Load Cell to Load Cell Handle Adapter and Load Cell Carriage)
2.31.4.5. M2.5-0.45 x 6-8mm Socket Cap Screws (CPX to CPX Holder and Qwiic Scale to Handle Base)
2.31.4.6. M3-0.5 mm hex nuts

### 3. Assembly Procedure

3.1. Download all STL files from Github. Print as specified (SLA or extrusion) in “Equipment and Terminology”

Load Cell Apparatus Assembly

3.2.Align hole of High Cube Intermediate Joint with top left hole (as viewed from back) of Load Cell Carriage (see pictures below).

3.3. Apply Krazy Glue on tip of M3-0.5 x 6mm screw. Insert screw into hole to connect High Cube Intermediate Joint and Load Cell Carriage. Press screw in firmly and put glue along edges of cube/carriage interface to reinforce hold. Allow glue to dry.

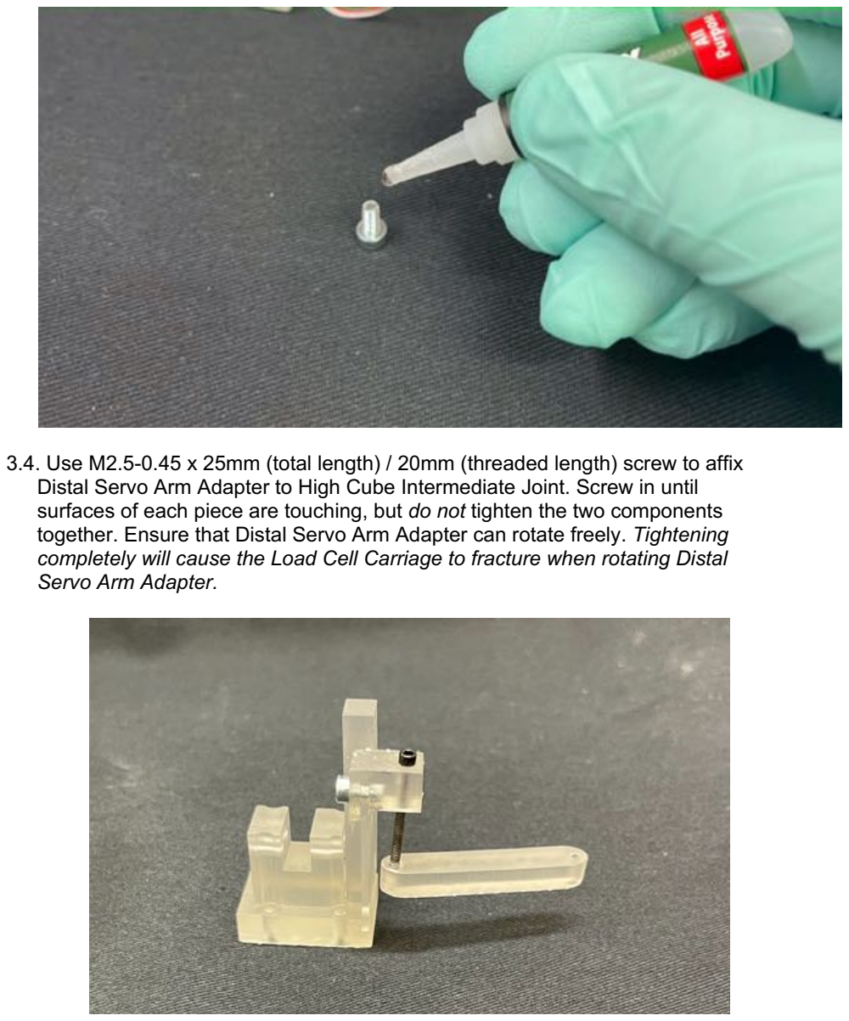
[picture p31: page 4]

3.4. Use M2.5-0.45 x 25mm (total length) / 20mm (threaded length) screw to affix Distal Servo Arm Adapter to High Cube Intermediate Joint. Screw in until surfaces of each piece are touching, but do not tighten the two components together. Ensure that Distal Servo Arm Adapter can rotate freely. Tightening completely will cause the Load Cell Carriage to fracture when rotating Distal Servo Arm Adapter.

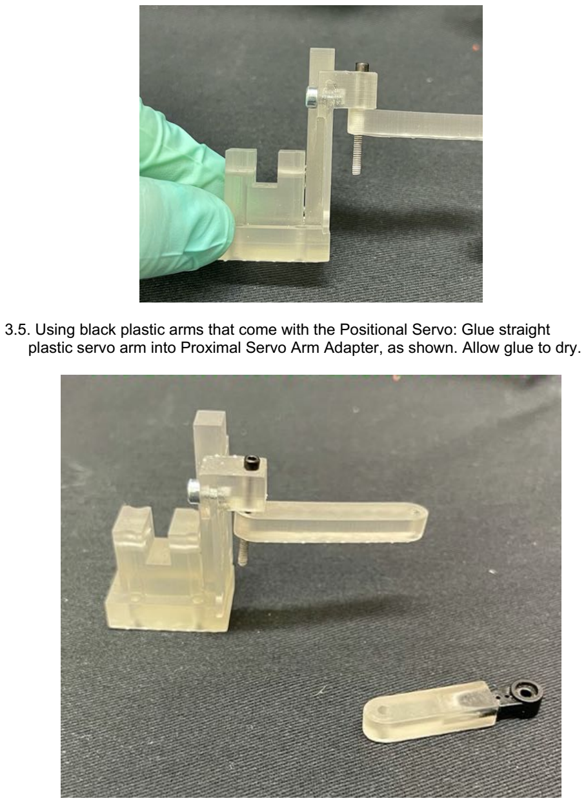
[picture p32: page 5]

3.5. Using black plastic arms that come with the Positional Servo: Glue straight plastic servo arm into Proximal Servo Arm Adapter, as shown. Allow glue to dry.

3.6.Connect Proximal Servo Arm Adapter to Distal Servo Arm Adapter with M2.5-0.45 x 25mm (total length) / 20mm (threaded length) screw, with the screw oriented upside-down as shown. Ensure that Proximal Servo Arm Adapter is oriented such that the hole with the notches on the black plastic servo arm is facing down (so that piece can later be plugged into servo). Screw in until the servo arm adapter surfaces are touching, but do not tighten. Ensure each piece can freely rotate.

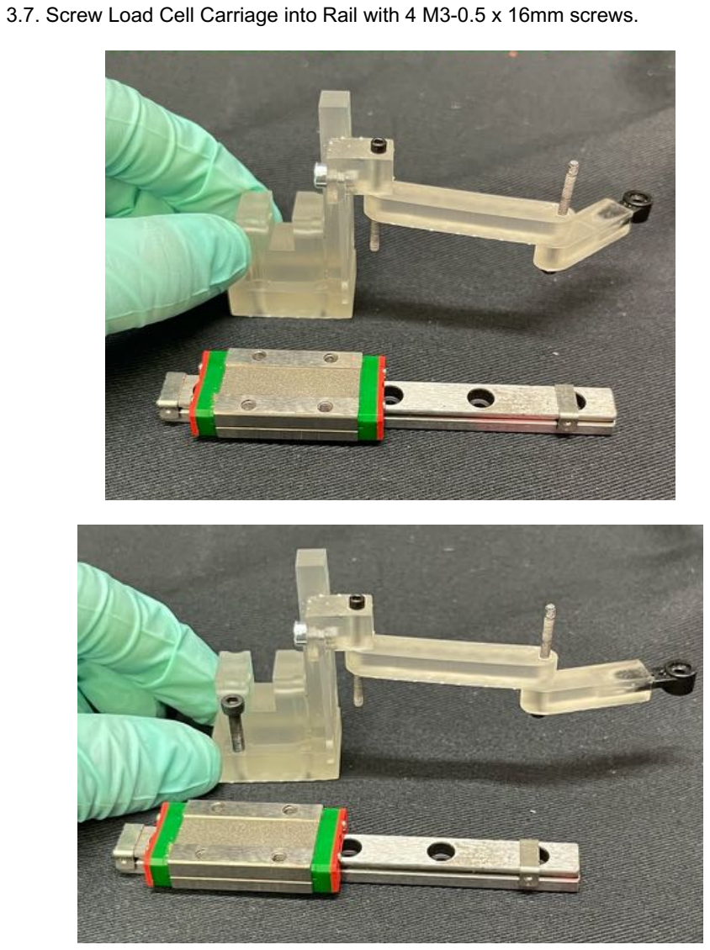
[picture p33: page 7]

3.7. Screw Load Cell Carriage into Rail with 4 M3-0.5 x 16mm screws.

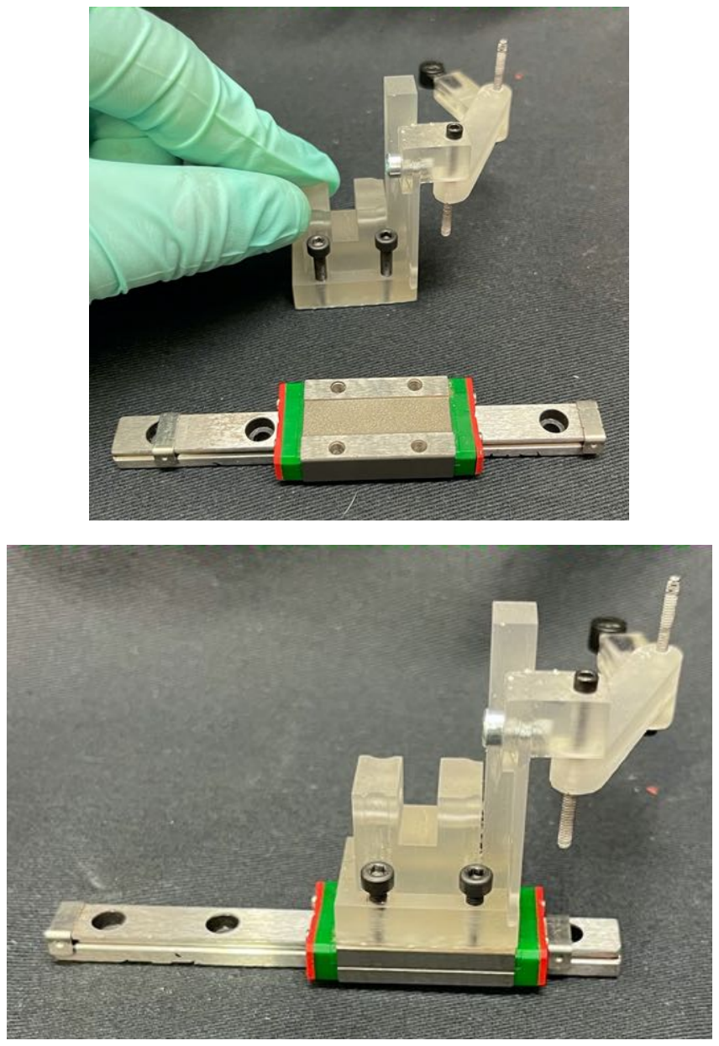
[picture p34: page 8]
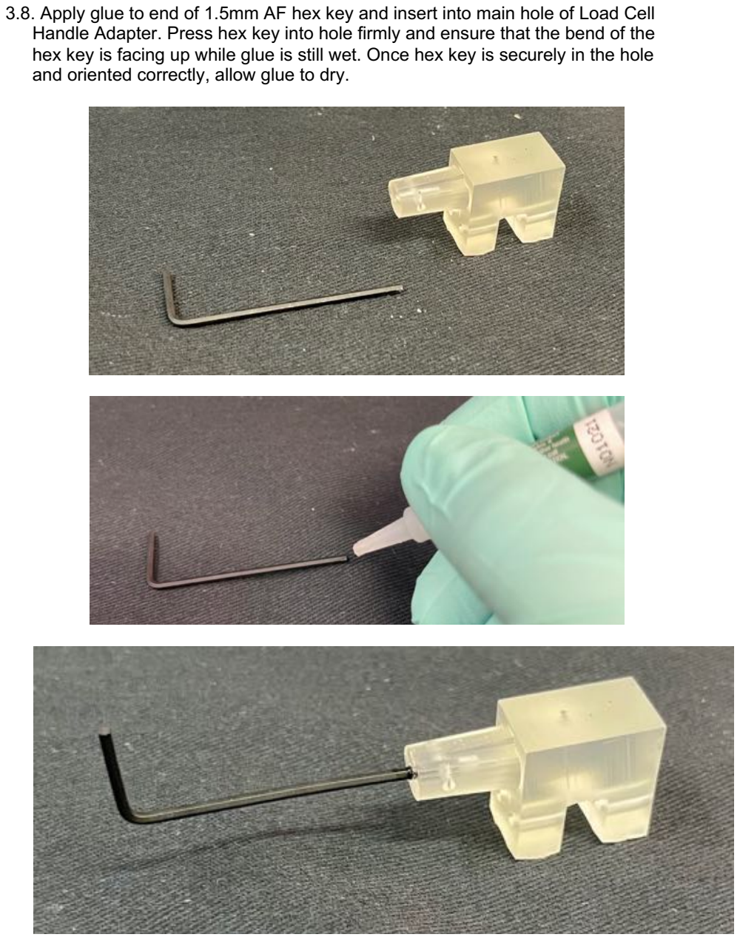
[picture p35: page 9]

3.8. Apply glue to end of 1.5mm AF hex key and insert into main hole of Load Cell Handle Adapter. Press hex key into hole firmly and ensure that the bend of the hex key is facing up while glue is still wet. Once hex key is securely in the hole and oriented correctly, allow glue to dry.

3.9.Screw top of Load Cell into Load Cell Handle Adapter with M2.5-0.45 x 25mm (total length) / 20mm (threaded length) screws. Recommended to wrap end of screw with Parafilm M to create a tighter fit.

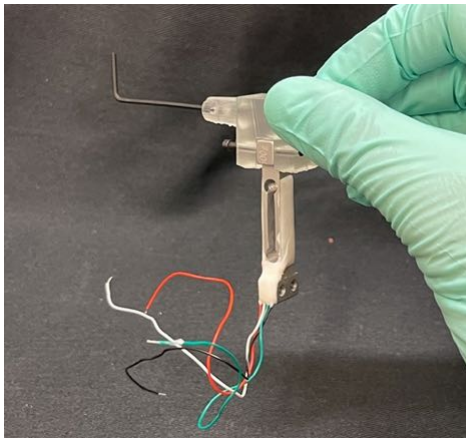
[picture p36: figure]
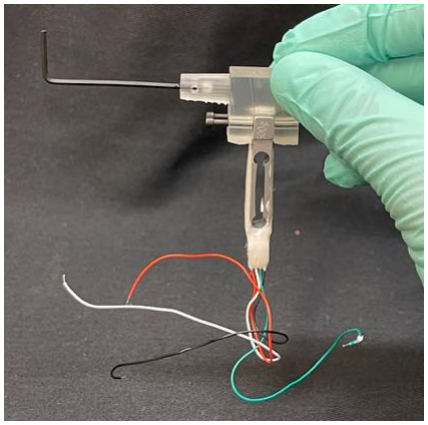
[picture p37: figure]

3.10.Screw Load Cell into Load Cell Carriage with M3-0.5 x 16mm screws. Recommended to wrap end of screw with Parafilm M to create a tighter fit.

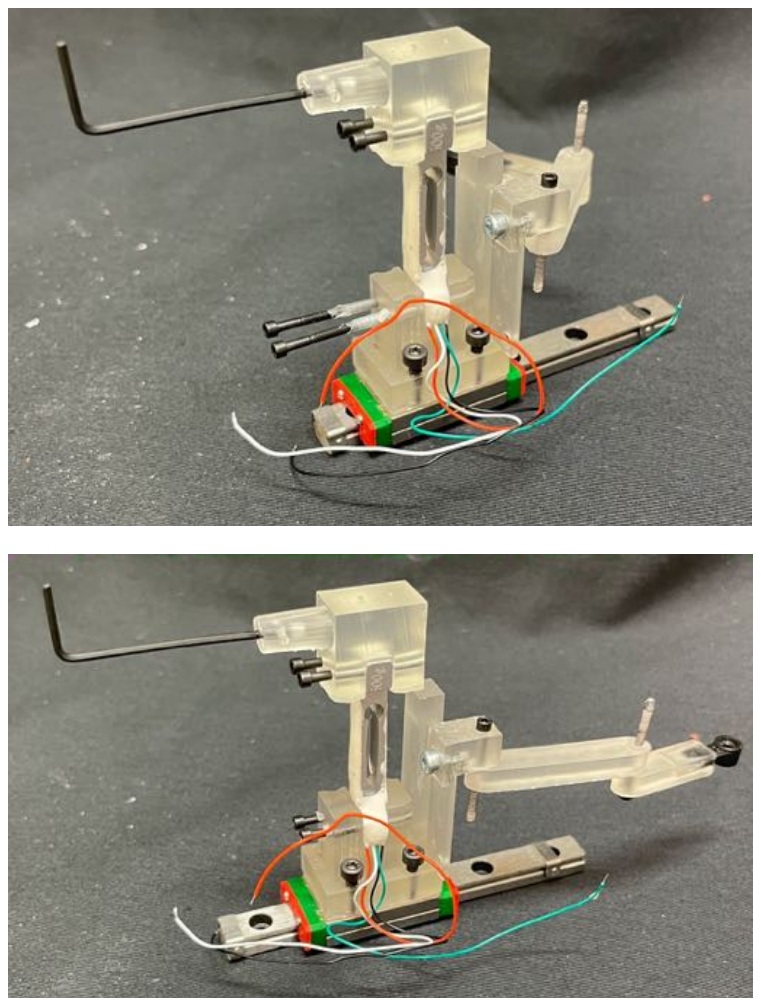
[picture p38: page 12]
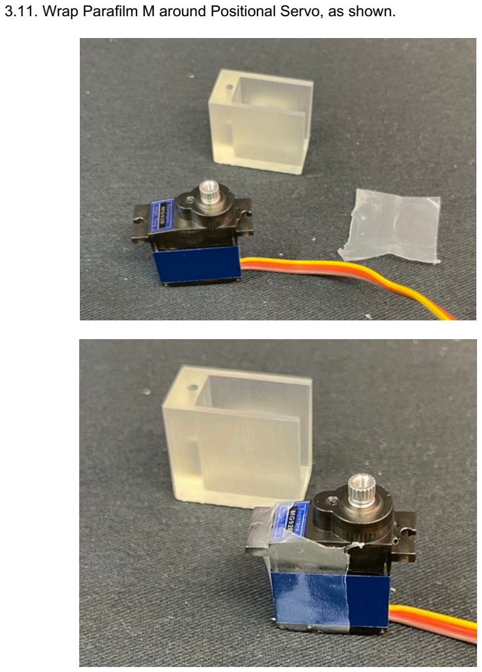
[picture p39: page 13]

3.11. Wrap Parafilm M around Positional Servo, as shown.

3.12. Insert Parafilm M-wrapped Positional Servo into Positional Servo Casing.

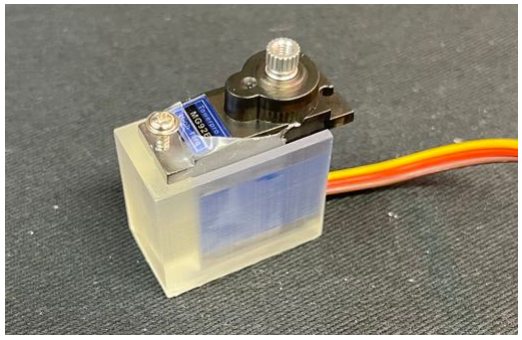
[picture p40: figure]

3.13. Fasten the Positional Servo into the Positional Servo Casing with the 7.5mm-long screw that comes with the commercial Positional Servo.
3.14. Align holes of Rail (which should now be connected to the Load Cell Apparatus) with the holes of the Handle Base. Place Positional Servo Casing (and enclosed Positional Servo) on the back insertion point on the Handle Base, with the front portion of the casing slightly covering part of the Rail.
3.15. Insert M3-0.5 x 12mm screws into holes of Rail and through the holes of the Handle Base. You will have to move Load Cell Carriage along rail to access all the screw holes.

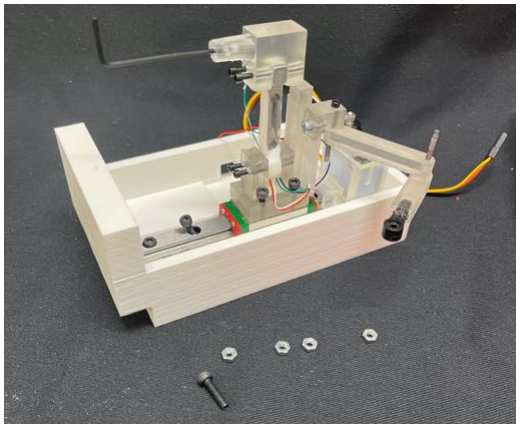
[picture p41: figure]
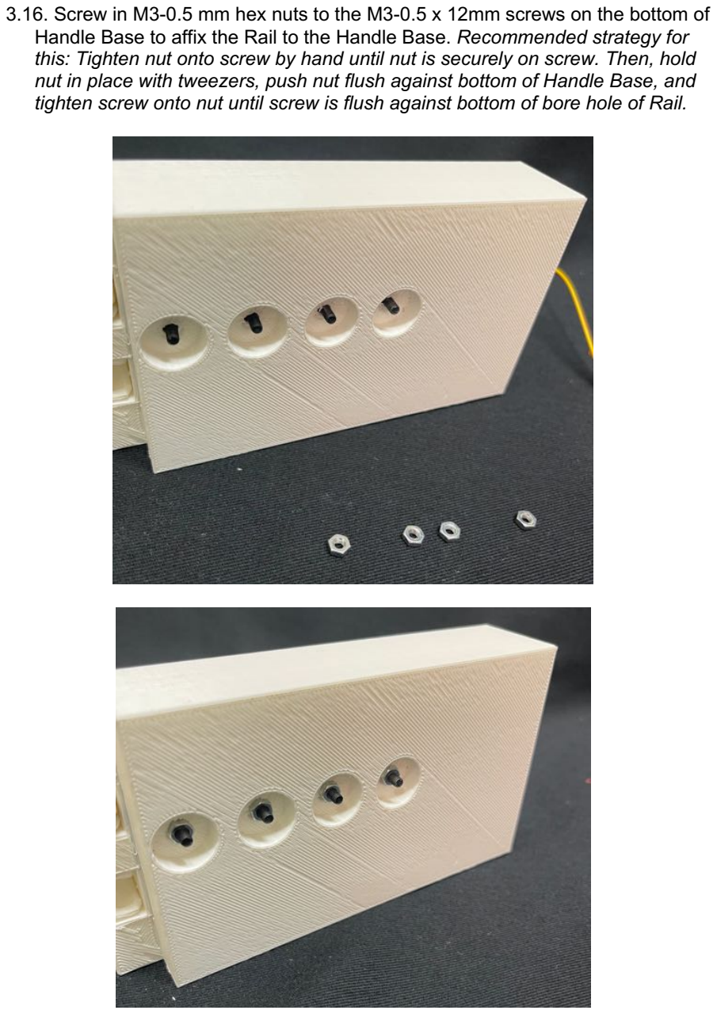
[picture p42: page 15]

3.16. Screw in M3-0.5 mm hex nuts to the M3-0.5 x 12mm screws on the bottom of Handle Base to affix the Rail to the Handle Base. Recommended strategy for this: Tighten nut onto screw by hand until nut is securely on screw. Then, hold nut in place with tweezers, push nut flush against bottom of Handle Base, and tighten screw onto nut until screw is flush against bottom of bore hole of Rail.

3.17. Move Load Cell Carriage to front of Rail and attach black servo arm to rotating piece of Positional Servo. You will likely need to re-attach this arm during first calibration so that the Load Cell Carriage is positioned at the front of the Rail when the Positional Servo is set to 0º (see AutoRG_Calibration_SOP).
3.18. Run 4 wires from Load Cell (red, white, green, black) through hole on bottom left (as viewed from back) of Load Cell Carriage.

3.19. Plug in Load Cell wires into corresponding port of Qwiic Scale (labeled on Qwiic Scale by color). Press orange lever down for corresponding plug hole, insert wire fully, and release lever. Tug on wire lightly to ensure that it is fully plugged into Qwiic Scale port.

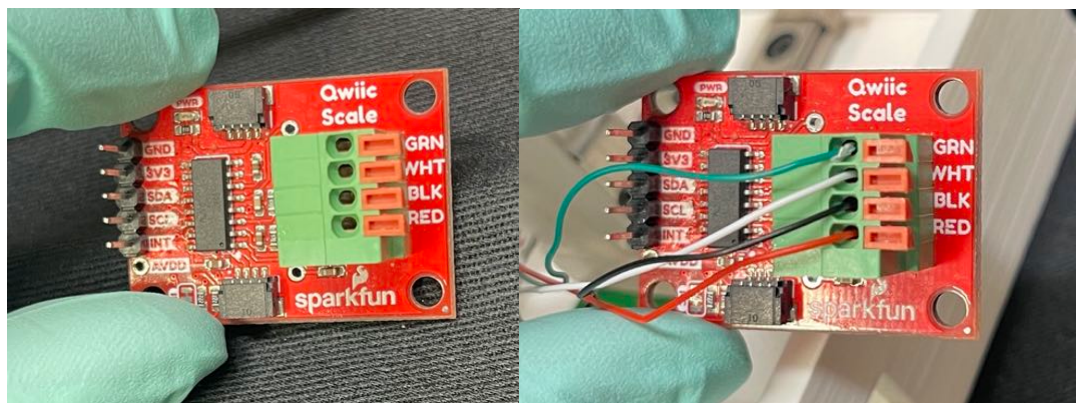
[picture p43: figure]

3.20. With ~75mm long insulated wires, solder 4 wires into SCL, SDA, 3.3V, and GND pins of Qwiic Adapter.
3.21. Connect 3.3V and GND wire from Qwiic Scale into 2 male pins. Plug male pins into corresponding 3.3V and GND female pin connector of CRICKIT board.
3.22. Loosen screws on SCL and SDA locations of CPX. Wrap corresponding SCL and SDA wires from Qwiic Scale underneath screw head and tighten screw onto wire so that a firm connection is established. Alternatively, solder each wire to a metal plate and screw each metal plate underneath corresponding screw.

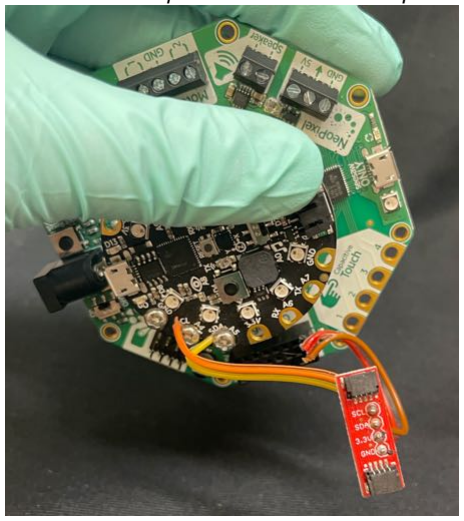
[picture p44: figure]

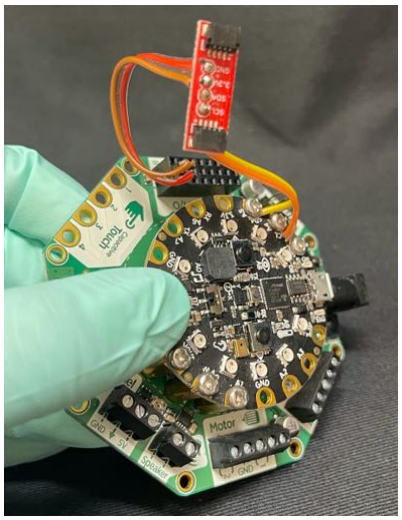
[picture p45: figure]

3.23. Place Qwiic Scale in its Handle Base indentation. Run STEMMA QT / Qwiic Cable through hole next to Qwiic Scale and connect cable to Qwiic Scale. Plug other end of STEMMA QT / Qwiic Cable into Qwiic scale, as shown.

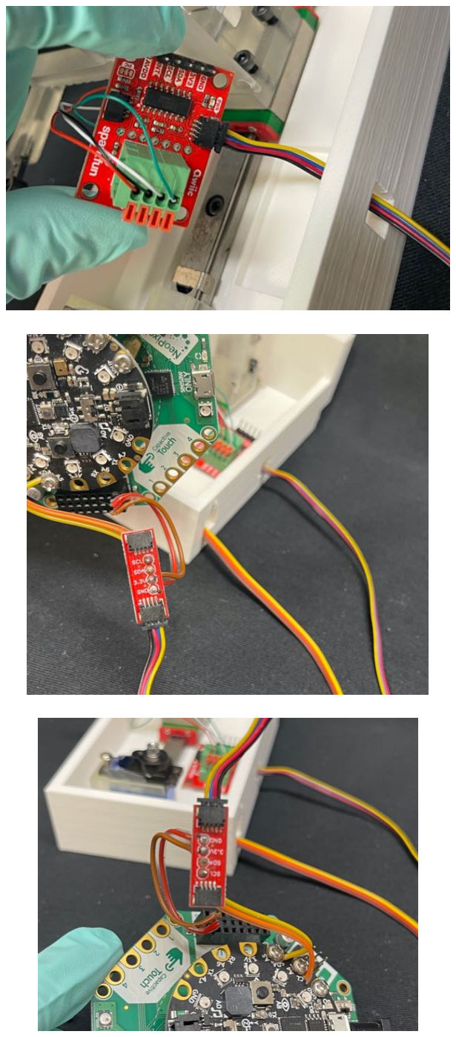
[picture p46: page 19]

3.24. Screw in Qwiic scale to Handle Base holes with M2.5-0.45 x 6-8mm screws.
3.25. Snap 4 quadrants of Stage together.
3.26. Snap Handle Base to front right quadrant of Stage.

Handle Base Positioned on Stage:

Handle Base Snapped into Stage

Pellet Dispenser Assembly

3.27. Wrap Parafilm M around top of Pellet Servo (continuous servo) as shown.

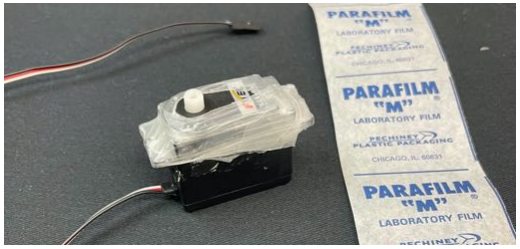
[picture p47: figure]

3.28. Insert Pellet Servo into Pellet Dispense Base.
3.29. Place notched Pellet Servo Actuator onto rotating component of Pellet Servo. Ensure notches are aligned and Pellet Servo Actuator is securely attached to rotating component of Pellet Servo.

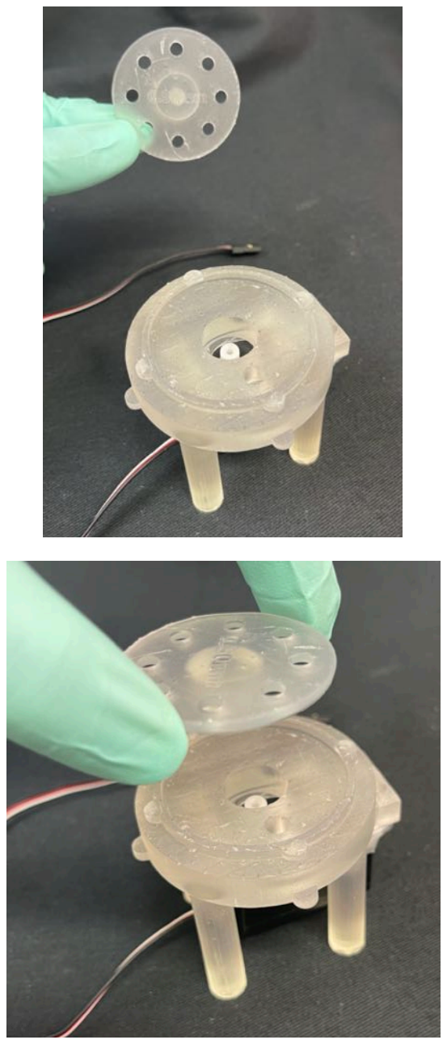
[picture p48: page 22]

3.29.1. Before proceeding: Ensure that servo will rotate properly (assuming software has been downloaded and initialized).
3.29.1.1. Plug Pellet Servo into “Servo” Row 2 spot on CRICKIT (black wire faces inward, white wire faces outward, as pictured below.
3.29.1.2. Turn on CPX, plug into power, and plug USB connection into computer
3.29.1.3. Boot up Calibration_GUI, and click “Run” on Editor tab of MatLab to open GUI.
3.29.1.4. Check COM port for CPX in computer’s “device manager” section. Enter corresponding COM code (e.g., COM5) and click “Connect” (see AutoRG_Calibration_SOP for more detailed instructions).
3.29.1.5. Click “Start Read”, and check that GUI is receiving load information from Load Cell in upper graph.
3.29.1.6. Click “Dispense Pellet”. Servo should rotate at least once; check that it rotates smoothly. If rotation continues rapidly, must calibrate Pellet Servo:
3.29.1.6.1. Insert Calibration Knob into hole of Pellet Servo (can be difficult to find exact hole). Rotate Calibration Knob and observe the spinning of the Pellet Servo to either increase in speed or decrease in speed. If speed does not change when knob is turned, readjust position of Calibration Knob in hole until it affects the spinning speed. Turn knob in direction that decreases speed of rotation and modulate turning of knob until Pellet Servo is not moving.

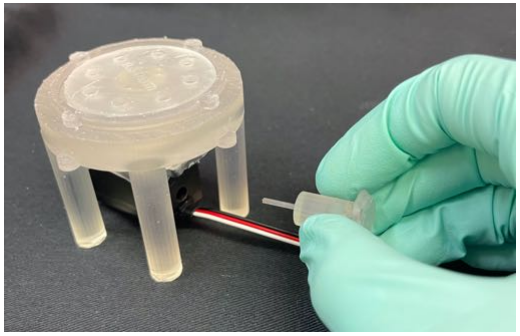
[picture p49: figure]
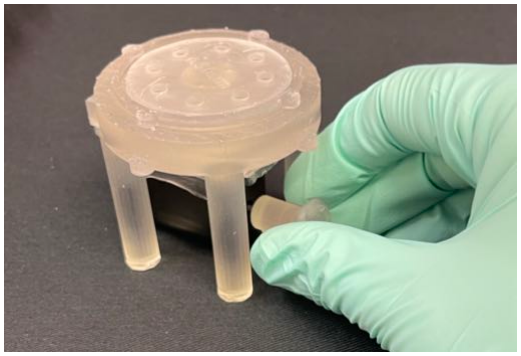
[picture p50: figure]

3.29.1.6.2. To check that calibration is complete: Click “Dispense Pellet” again. Pellet Servo should rotate once and stop after.
3.30. Place glue on bottom edges of Food Silo and top edges of Pellet Dispense Base and adhere Food Silo to this Pellet Dispense Base. Take care to ensure glue does not spill onto Pellet Servo Actuator component, or rotation will be impaired. Ensure that Food Silo is oriented correctly on the Pellet Dispense Base (the dispense hole on base should be covered by the semicircle of the Food Silo). Turn upside down (top of Food Silo facing down) and allow glue to dry.

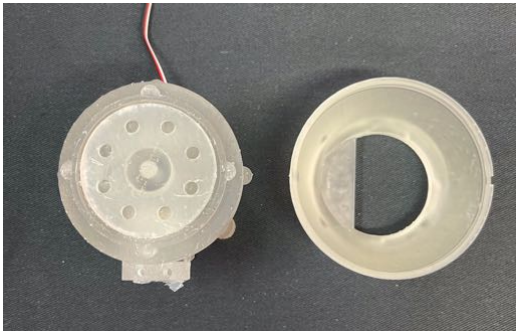
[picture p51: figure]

3.31. Snap Pellet Dispense Tower into the front left quadrant of the Stage.
3.32. Place Pellet Dispenser on top of Pellet Dispense Tower. Run wire of Pellet Servo out of hole on top of tower.

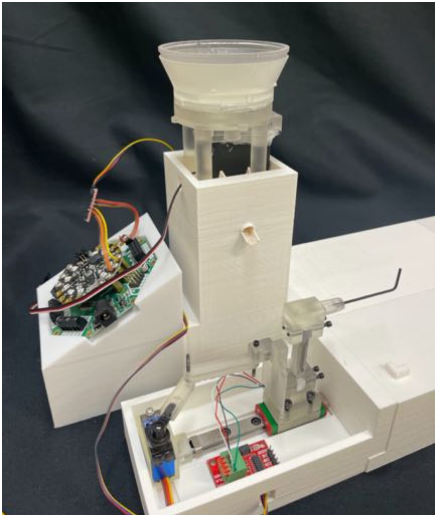
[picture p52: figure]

Final Assembly Steps

3.33. Snap CPX Holder into back of Pellet Dispenser Tower.
3.34. Place CPX/CRICKIT into position on CPX Holder. Screw CRICKIT into holes with M2.5-0.45 x 6-8mm screws.

3.35.Plug in Pellet Servo into Row 2 of “Servo” section on CRICKIT (black wire on inner pin, white wire on outer pin).

3.36. Run wire of Positional Servo through nearby hole on Handle Base, and plug into Row 1 of “Servo” section on CRICKIT (brown wire on inner pin, yellow wire on outer pin).

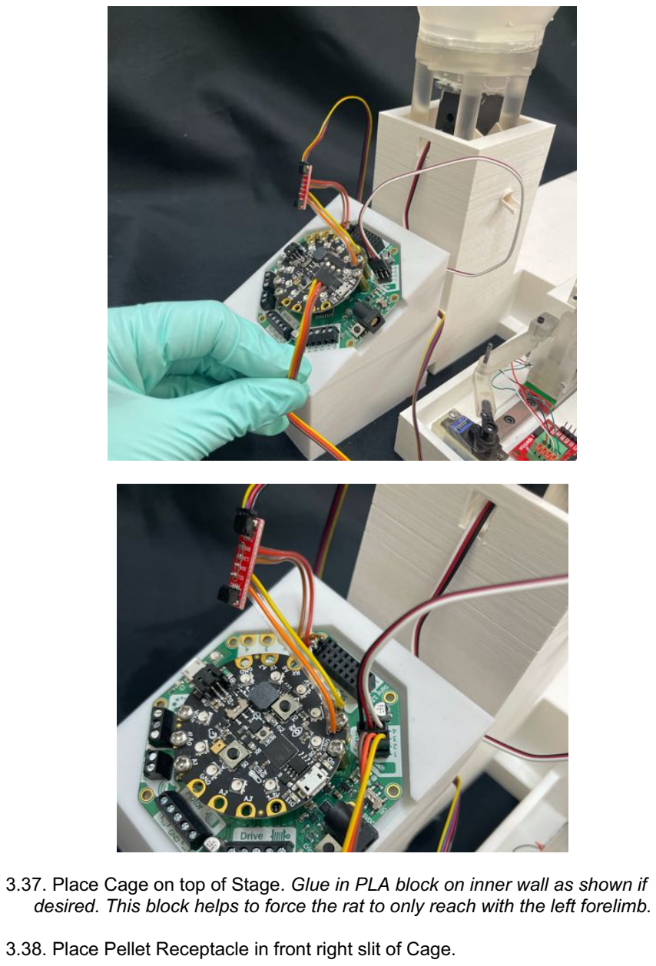
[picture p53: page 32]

3.37. Place Cage on top of Stage. Glue in PLA block on inner wall as shown if desired. This block helps to force the rat to only reach with the left forelimb.
3.38. Place Pellet Receptacle in front right slit of Cage.

3.39. Cut Pellet Tubing (outer diameter: 12.5mm, inner diameter: 9.5mm) to ~94mm in length. Run piping from opening of Pellet Receptacle to opening of Pellet Dispense Tower.
